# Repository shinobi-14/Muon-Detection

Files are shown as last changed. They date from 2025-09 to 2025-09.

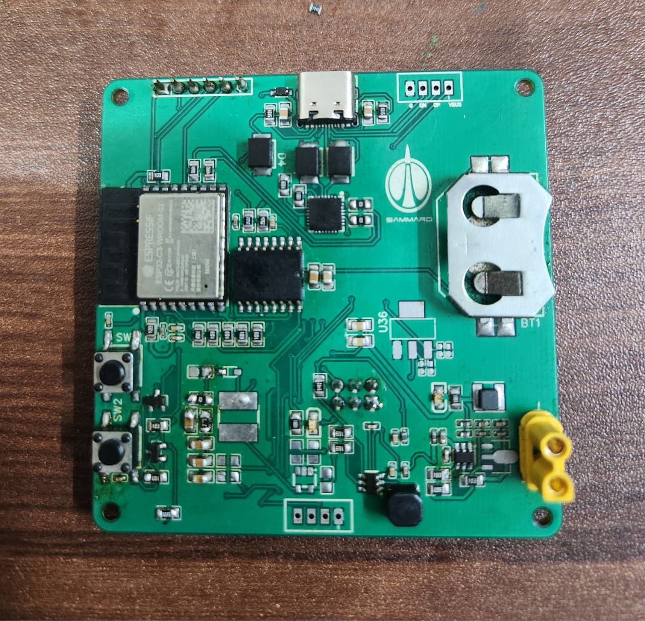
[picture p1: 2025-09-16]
media/images/Soldered_PCB_previews/1.) PCB_top.jpg

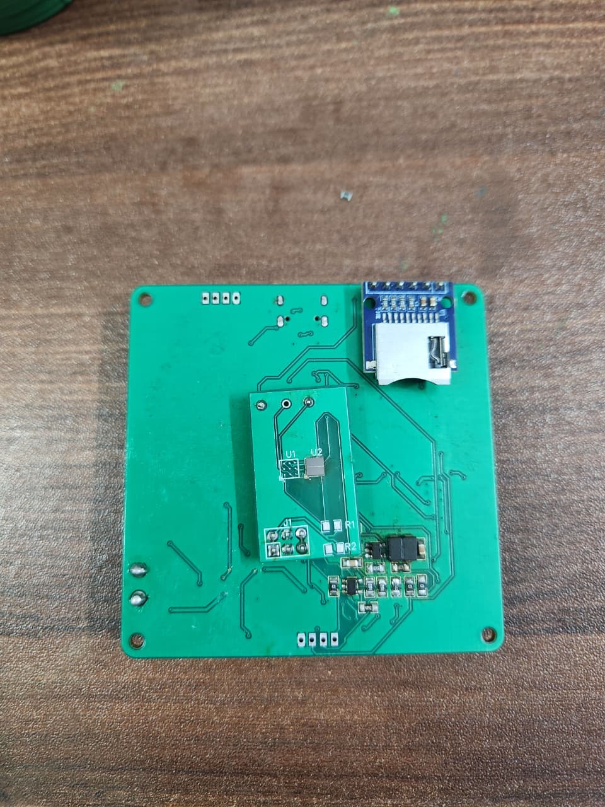
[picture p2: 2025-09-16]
media/images/Soldered_PCB_previews/2.) PCB_bottom.jpg

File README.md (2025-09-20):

# Muon-Detection
Muon-Detection, an independent subsystem of Project STRIVE developed for the SDL Payload Challenge, serves as a payload on the sounding rocket Airavata in IREC 2025.
<div align="center">
  
</div>

The Muon-Detection system incorporates a commercial and a student-designed 3D-printed scintillator (developed in collaboration with IIT Roorkee) to measure muon flux along the rocket's trajectory, enabling performance comparison and supporting real-time tomography simulations for potential non-destructive testing during sonic and supersonic flight.

## Detector Architecture
#### 1. Commercial Scintillator Setup
<div align="left">
  
</div>
    
- Scintillator: BC-408 plastic scintillator (known for its high light yield and fast decay time)
- Photo-detector: 3mm × 3mm BROADCOM's AFBR-S4N33C013  SiPM (Silicon Photomultiplier)
- Associated Electronics

#### 2. Experimental 3D Printed Scintillator
<div align="left">
  
  
</div>

- Scintillation Components: Incorporated 2,5-diphenyloxazole (PPO) and a wavelength shifter.
- Scintillator Fabrication: Used an acrylate photo-curing monomer with aromatic rings as the base matrix.
- 3D Printing Process: Added a small amount of BAPO photo-initiator, poured the mixture into the 3D-printer VAT, and printed 100 µm layers sequentially (on top of each other) to form the final structure.

## SiPM Main PCB
The SiPM PCB is designed to interface with Silicon Photomultipliers (SiPMs) for detecting scintillation events. 
<div align="center">
  
  
</div>

SiPM output signals are typically weak, so this PCB includes a carefully designed amplifier circuit that boosts the signal strength while preserving its integrity. 

The amplifier matches the SiPM’s voltage and current characteristics, ensuring a clean, low-noise signal that maintains the peak amplitude of fast analog pulses for accurate processing by the onboard microcontroller. 

Additionally, the PCB provides stable biasing and reliable signal routing to the data acquisition system, making it a critical component of the payload’s detection and readout chain.

## Repo Structure
The PCB was designed entirely in EasyEDA. I've included the design files, 3D files, gerber, schematic, test codes, media files and testing materials.

To replicate or explore this project, download the repository files and open them in EasyEDA, ensuring all file paths are correctly linked.
    
	1. 3D_files
		a. SIPM main PCB | SIPM small PCB
			- .mtl & .obj 3D exports for 3D visualization and mechanical fit checks.
	
	2. Design_Files 
		a. SIPM main PCB | SIPM small PCB
			i. Altium_Design_files - Exports from EasyEDA for Altium compatibility.
			ii. Autorouter_files - Auto-generated routing results.
			iii. EasyEDA_Design_files - Original PCB designs.
			iv. Export_Netlist_files - Netlists for simulation and validation.
		
	3. Fabrication_files 
		a. SIPM main PCB | SIPM small PCB
			i. Gerber files - Standard files for PCB manufacturing.
			ii. BOMs.csv - List all components used in this project.
			iii. PickAndPlace.csv - Data for automated assembly.
		
	4. Schematics
		a. SIPM main PCB | SIPM small PCB
			i. schematic.pdf - Readable schematic.
			ii. schematic.svg - Scalable/vector schematic.
	
	5.  media
		a. images - Renders, test setups, and PCB visuals.
		b. testing videos - Muon-Detection tests under different conditions.
		
	6. test codes
		All the test codes used during testing.
		
	7. testing materials
		Contains test records, analysis, and performance evaluation of commercial and 3D-printed scintillators.

 ## Components Used
 - AFBR-S4N33C013 SiPM (Silicone Photomultiplier)
 - BC-408 (Plastic Scintillator)
 - 3D-printed Scintillator
 - MIC2288 (DC-DC Boost Converter @ 33V)
 - DS3231 (Real Time Clock)
 - OPA356 (Operational Amplifier)
 - XT30 (Overload connector @ 30A)
 - SD Card Reader module
 - ESP32 C3 (32bit-microcontroller)
 - HT7833 (LDO Regulator @ 3.3V) - Redundant
 - AMS1117 (LDO Regulator @ 5V) - Redundant
 - CP2102 (UART Interface)
 - TPS56321 (Switching regulator @ 3.3V | @ 5V)

## Key Takeaways
1. It is not possible to couple two scintillators together, as there will be an immense amount of light loss at the boundary. 
2. This is the same region where we require large single crystals instead of smaller crystals coupled together. 
3. The scintillator can be coupled to the SiPM using optical-grade silicone gel/glue provided by companies such as Eljen (EJ-550, EJ-552) or Epic crystals.
4. There is a degradation of the additively manufactured scintillator with time. 
5. With temperature fluctuations, the scintillator could potentially lose its scintillation effect and overall effectiveness.
6. The PCB for the payload is designed for signal integrity, but the efficient functioning of the system in the scope of sounding rocket flight might be affected by the level of EM interference in the PCB. Therefore, readings might get affected due to this.
7. The muon detection system relies on the duration during which the rocket descends. There is a potential problem where the system can work efficiently only while it is at a specific altitude for a specific period of time.
8. While testing, I noticed that for BC-408 and 8.2 mm, squiggles are fewer compared to 3.9 mm and 6.2 mm. As the width increases, properly distinct peaks can be observed, which means thicker the sample, the farther the particle can penetrate through, so more efficient production of photons.

## Reference Materials 
- [SiPM Datasheet](https://www.farnell.com/datasheets/3096135.pdf?_gl=1*1ttkvz9*_gcl_au*MTI4NTU5OTYwNS4xNzQzNzAwNDU1)
- [OPA356 Datasheet](https://www.ti.com/lit/ds/symlink/opa356.pdf?ts=1746455532552&ref_url=https%253A%252F%252Fwww.google.com%252F)
- [Peak Detection Circuit](https://www.youtube.com/watch?v=w4531AVjBYY) (Highly Recommended)
- [britishastronomical Youtube](https://www.youtube.com/watch?v=j74CbXHByrY)
- [Front-end Electronics for SiPM](https://physicsopenlab.org/2017/11/28/front-end-electronics-for-sipm/)
- [Cosmic Watch Muon-Detector](https://github.com/spenceraxani/CosmicWatch-Desktop-Muon-Detector-v2/blob/master/PCB_Files/callibration.pdf) (Highly Recommended)
- [RD-Gammaspectra](https://www.youtube.com/watch?v=t7-f01MC4a4&t=58s) (Highly Recommended)
- [Current to Voltage Converotr](https://ecstudiosystems.com/discover/textbooks/basic-electronics/operational-amplifiers/current-to-voltage-converter/)
- [Mini SIPM Driver Board](https://hackaday.io/project/188090-mini-sipm-driver-board)
- [Muon Tomography Simulation](https://github.com/dimitra97/MuonTomographySimulation)
- [ComSAD](https://ar5iv.labs.arxiv.org/html/2110.12500)
- [Data acquisition system for the readout of SiPM arrays](https://ieeexplore.ieee.org/abstract/document/6829735) (Highly Recommended)

Author: Prithvi Raj Singh (shinobi-14)

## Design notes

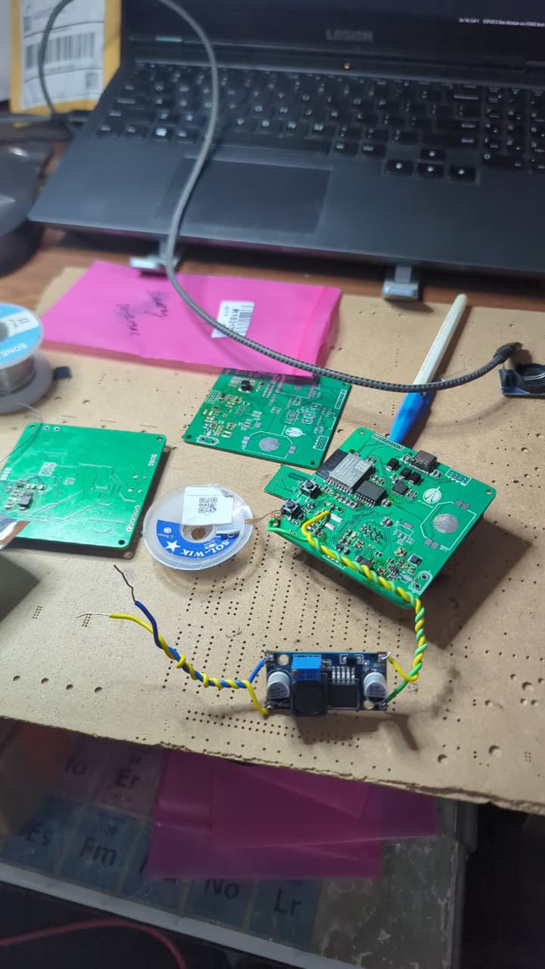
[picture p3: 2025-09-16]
media/images/Workbench.jpg

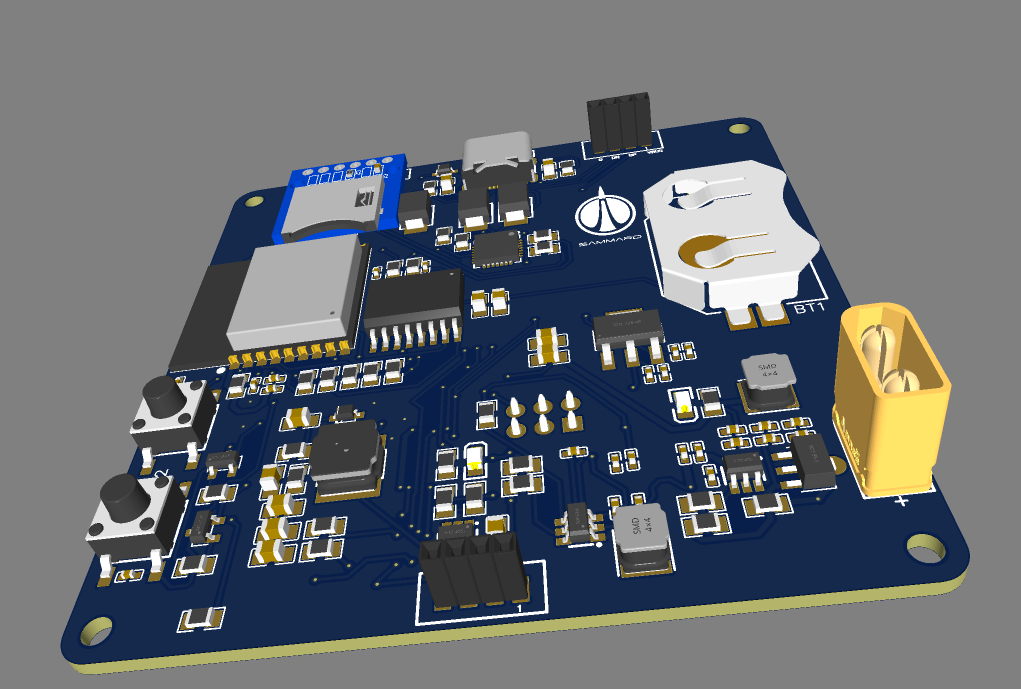
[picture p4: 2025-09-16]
media/images/3D_previews/1.) 3D_SIPM.png

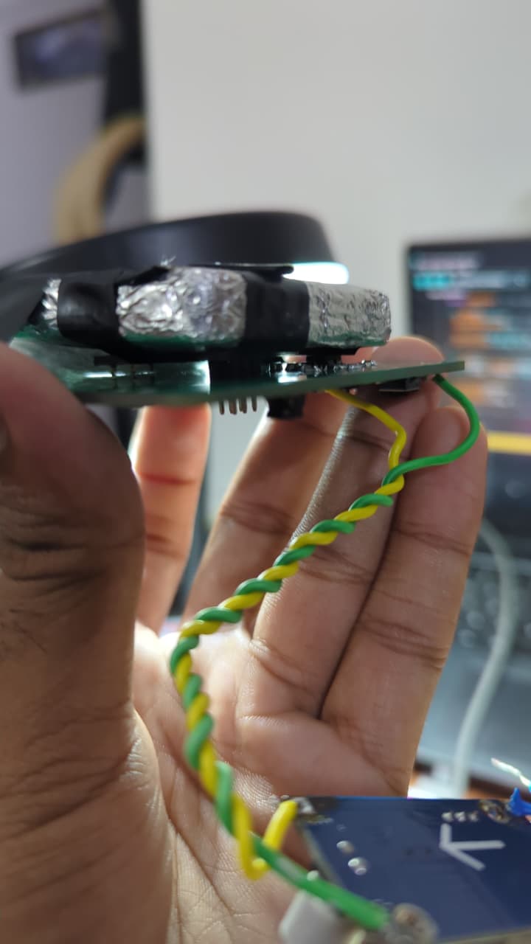
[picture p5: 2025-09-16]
media/images/Scintillator/Scintillator_wrapped_with_foil.jpg

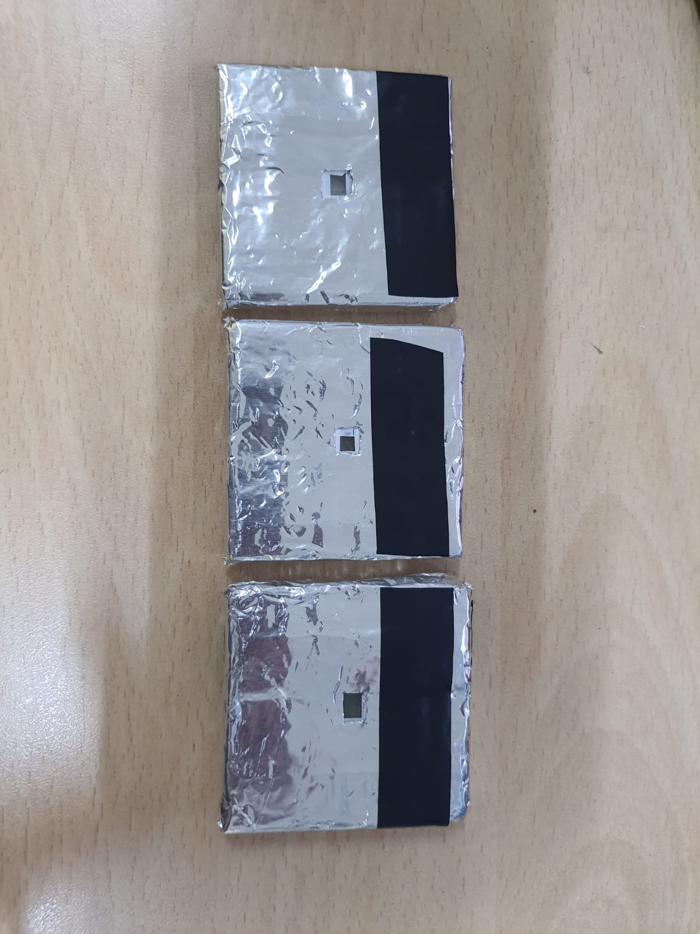
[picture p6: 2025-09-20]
media/images/Scintillator/Scintillator(2).jpg

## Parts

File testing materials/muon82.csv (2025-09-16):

components | package | 1
1.5uH | 603 | 1
AMS 3.3 |  | 1
TPS63030 |  | 1
35.7K | 603
AMS 5
1uF | 805
MCP16311
1.5uH power inductor
56K | 805
10uF | 805
22uH power inductor
220 ohms | 805 | BESSV2
4.7K | 805 | BESSV2
10K | 805 | BESSV2
1N4007 |  | BESSV2
6pF | 603
10uF | 805
100nF | 805
22uF | 805
dual mosfet P
AMS 3.3
5.1K | 805
7.5nH | 402
power usb c
ams 5
1uF | 805
0.1uF | 805
1.2K | 805 | PDB
3.3uH power inductor |  | PDB
20K | 805 | PDB
54.9K | 603 | PDB
12k | 603
0 ohms | 805
130 ohms | 805
100 ohms | 805
10K | 805
0.1uF | 603
0.1uF | 805
10uF | 805
blue led | 805
red led | 805
10uF | 1206
22uF | 1206
1K | 805
esp32 c6
battery charging board
switches
INSPACE BOX - untouched
2.2uF | 603 | SHROTA v2
type c power |  | SHROTA v2
ESD diode | DO214AA | SHROTA v2
100nF | 603 | SHROTA v2
1K | 603
4.7K | 603
22uF | 603
22 ohms | 603
5.1K | 603
HT7833 LDO 3.3 SOT-235
6.5pF | 603
7.5uH | 402
1.5uH | 603
10K | 603
10uF | 603
antenna 915MHz
HT7833 LDO 3.3 SOT-89 3
Diodes 1n4007ws
ws2812b
female to sma

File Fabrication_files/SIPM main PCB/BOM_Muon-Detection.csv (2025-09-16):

ID | Name | Designator | Footprint | Quantity | Manufacturer Part
1 | CR2032 | BT1 | BAT-SMD_CR2032 | 1 | CR2032
2 | 0.1uF | C1,C7,C10,C12,C14 | C0805 | 5 | 0805B203K500NT
3 | 10uF | C2,C8,C11,C13,C16 | C0805 | 5 | 0805B203K500NT
4 | 4.7uF | C3 | C0805 | 1 | 0805B203K500NT
5 | 2.2uF | C4 | C0805 | 1 | 0805B203K500NT
6 | 20nF | C5,C6,C9 | C0805 | 3 | 0805B203K500NT
7 | 1uF | C15,C17 | C0805 | 2 | 0805B203K500NT
8 | XT30UPB-M | CN1 | CONN-TH_XT30UPB-M | 1 | XT30UPB-M
9 | 1N5819WS | D1 | SOD-323_L1.8-W1.3-LS2.5-RD | 1 | 1N5819WS
10 | LBAT54HT1G | D2 | SOD-323_L1.8-W1.3-LS2.5-RD | 1 | LBAT54HT1G
11 | 1N5817W | D3,D7 | SOD-123_L2.8-W1.8-LS3.7-RD | 2 | 1N5817W
12 | SMBJ7.5CA-QH | D4,D5,D6 | DO-214AA_L4.4-W3.6-LS5.3-BI | 3 | SMBJ7.5CA-QH
13 | 2×(4-1) Double female header | H1 | HDR-TH_6P-P2.54-V-F-R2-C3-S2.54-1 | 1 | 2×(4-1) Double female header
14 | 10uH | L1 | IND-SMD_L6.0-W6.0_FNR60XXS | 1 | SWPA6028S100MT
15 | 2.2uH | L2 | IND-SMD_L4.0-W4.0_SMNR4012 | 1 | SWPA4030S3R3MT
16 | 3.3uH | L3 | IND-SMD_L4.0-W4.0_SMNR4012 | 1 | SWPA4030S3R3MT
17 | SD card Reader | P1 | HDR-TH_6P-P2.54-V-F | 1 | 2.54-1*6P母
18 | L8050QLT1G | Q1,Q2 | SOT-23-3_L2.9-W1.3-P1.90-LS2.4-BR | 2 | L8050QLT1G
19 | 10k | R1,R2,R11,R14,R18,R22,R33,R34,R35 | R0805 | 9 | 0805
20 | 10K | R3,R6,R7,R19,R20 | R0805 | 5 | 0805
21 | 2k | R4 | R0805 | 1 | 0805
22 | 33.2k | R5 | R0805 | 1 | 0805
23 | 1k | R8,R31,R32,R43 | R0805 | 4 | 0805
24 | 51k | R9 | R0805 | 1 | 0805
25 | 499 | R10,R13 | R0805 | 2 | 0805
26 | 0805 | R12,R17,R21,R23,R24,R25,R26,R27,R37,R41,R42 | R0805 | 11 | 0805
27 | 5.1k | R15,R16 | R0805 | 2 | 0805
28 | 0Ω | R28,R29 | R0805 | 2 | 0805
29 | 54.9k | R30 | R0805 | 1 | 0805
30 | 22.1K | R36 | R0805 | 1 | 0805
31 | 47.5K | R38 | R0805 | 1 | 0805
32 | 0Ω | R39,R40 | R0805 | 2 | FRC0805P000 TS
33 | SMD Tactile Switch6*6*6mm | SW1,SW2 | SW-SMD_4P-L6.0-W6.0-P4.50-LS9.0_C23873 | 2 | 贴片轻触开关6*6*6mm
34 | JST-PH_4-PIN_HEADER | U1,U17 | JST_B4B-PH_HEADER | 2
35 | 0.1uF | U2,U5,U10,U18,U20,U27,U32,U34,U37,U40 | C0402 | 10 | GRM155R71E103KA01D | SMD Ceramic Capacitor
36 | TPS563201DDCR | U3,U21 | SOT-23-6_L2.9-W1.6-P0.95-LS2.8-BR | 2 | TPS563201DDCR
37 | 10uF | U4,U11,U22,U28,U31,U33,U38,U39 | C0402 | 8 | GRM155R71E103KA01D | SMD Ceramic Capacitor
38 | MIC2288YD5-TR | U6 | TSOT-23-5_L2.9-W1.6-P0.95-LS2.8-BR | 1 | MIC2288YD5-TR
39 | ESP32-C3-WROOM-02-N4(4MB) | U7 | BULETM-SMD_ESPRESSIF_ESP32-C3-WROOM-02-N4-4MB | 1 | ESP32-C3-WROOM-02-N4
40 | 22uF | U8,U9,U24,U25 | C0402 | 4 | GRM155R71E103KA01D | SMD Ceramic Capacitor
41 | 1uF | U12,U13,U35 | C0402 | 3 | GRM155R71E103KA01D | SMD Ceramic Capacitor
42 | OPA356AIDBVR | U14,U15 | SOT-23-5_L3.0-W1.7-P0.95-LS2.8-BR | 2 | OPA356AIDBVR
43 | 0805 SF-RED | U16,U29,U41 | LED0805-RD_RED | 3 | 0805 SF-Red
44 | DS3231 | U19 | SO16W | 1
45 | CP2102 | U23 | QFN-28_L5.0-W5.0-P0.50-TL-EP3.2 | 1 | CP2102
46 | HT7833 | U26 | SOT-89_L4.5-W2.5-P1.50-LS4.2-BR | 1 | HT7833
47 | Sipm2 | U30 | SIPM_REVERSE | 1
48 | AMS117-5V | U36 | AMS117-TOPL | 1
49 | HX TYPE-C 16P 3MD 5A | USB1 | TYPE-C-SMD_HX-TYPE-C-16P-3MD-5A | 1 | HX TYPE-C 16P 3MD 5A

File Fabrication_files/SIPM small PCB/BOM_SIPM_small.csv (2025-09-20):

ID | Name | Designator | Footprint | Quantity
1 | Header-Male-2.54_2x3 | J1 | HDR-TH_6P-P2.54-V-M-R2-C3-S2.54-1 | 1
2 | 0Ω | R1,R2 | R0805 | 2
3 | NO | U1 | SIPM_ORI | 1
4 | Sipm2 | U2 | SIPM_REVERSE | 1

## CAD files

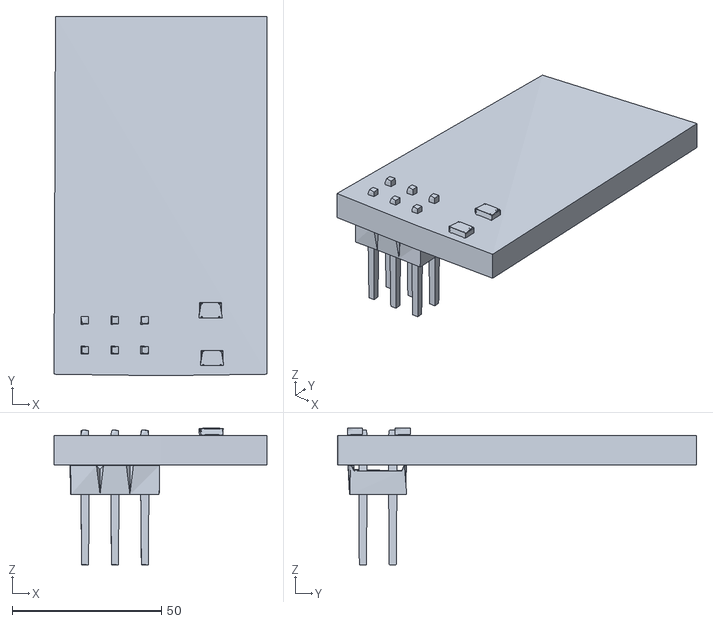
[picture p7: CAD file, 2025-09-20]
3D_Files/SIPM small PCB/OBJ_SIPM_small.obj
71.3 x 120.3 x 45.8

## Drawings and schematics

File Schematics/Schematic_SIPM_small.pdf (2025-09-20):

# SIPM PCB

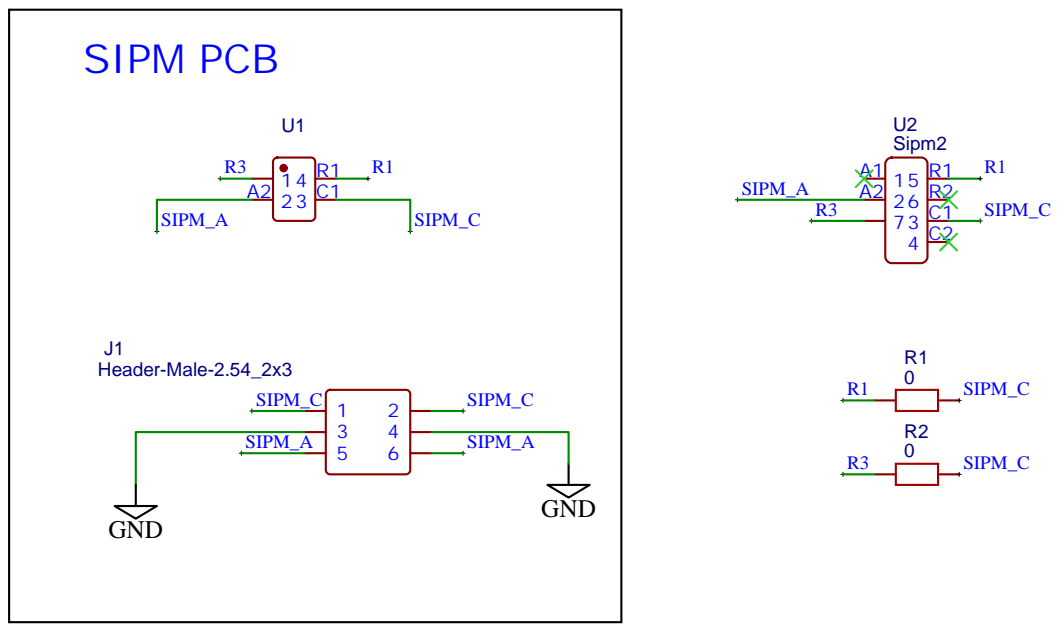
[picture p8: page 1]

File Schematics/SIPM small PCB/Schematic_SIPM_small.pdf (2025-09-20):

# SIPM PCB


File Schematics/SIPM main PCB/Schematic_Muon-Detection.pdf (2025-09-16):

# DC-DC Booster

# GND GND ³V3

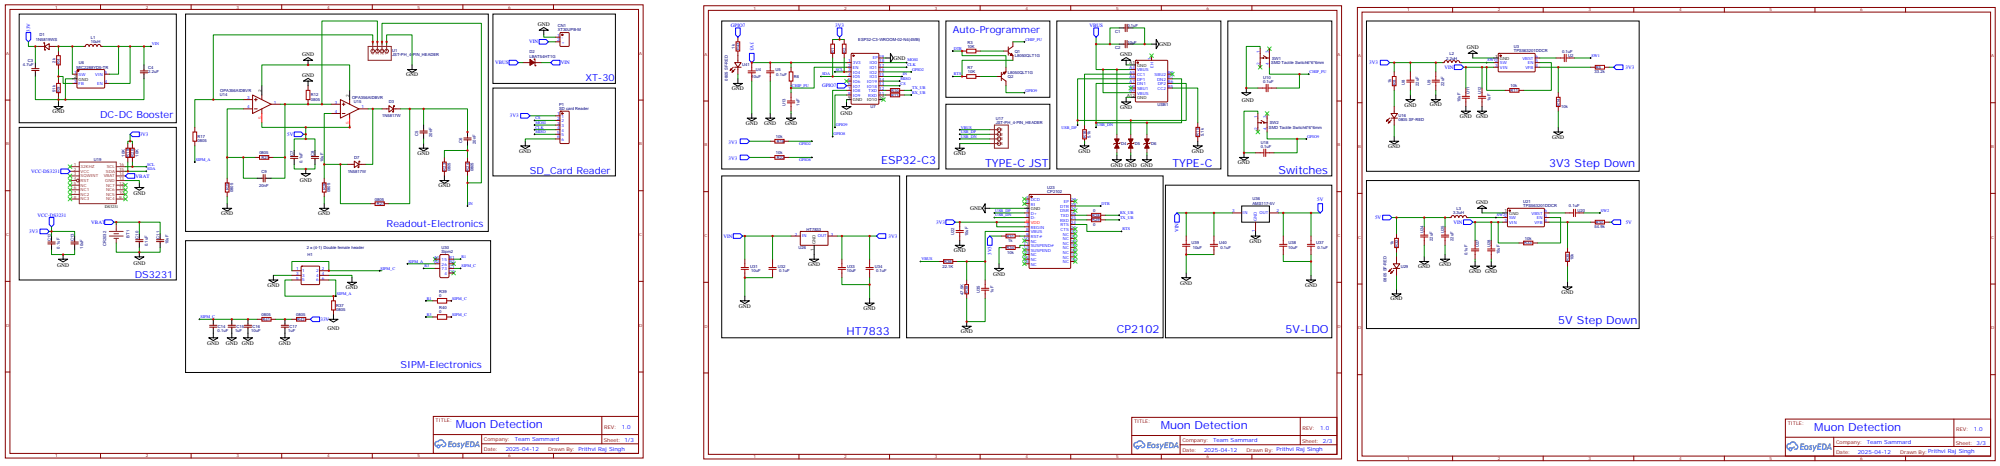
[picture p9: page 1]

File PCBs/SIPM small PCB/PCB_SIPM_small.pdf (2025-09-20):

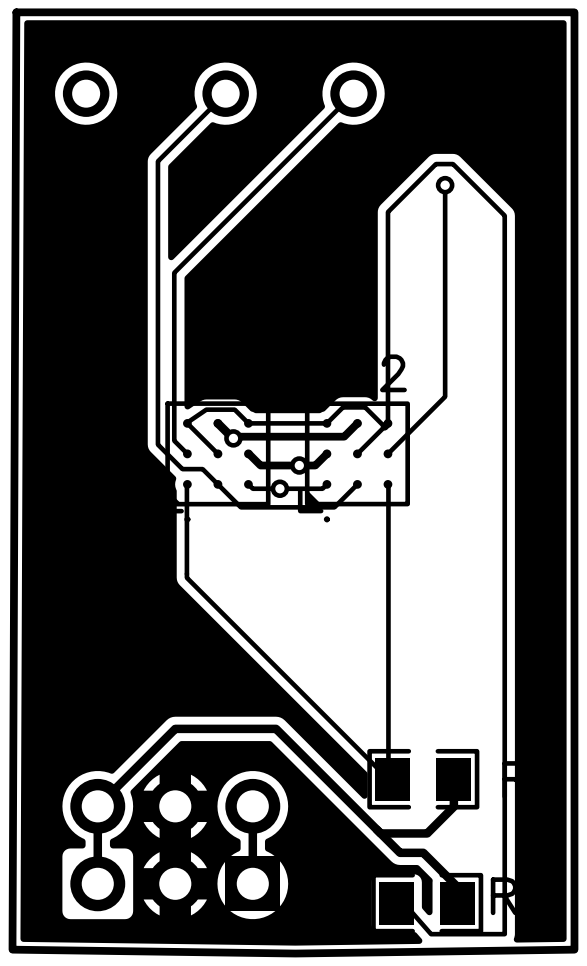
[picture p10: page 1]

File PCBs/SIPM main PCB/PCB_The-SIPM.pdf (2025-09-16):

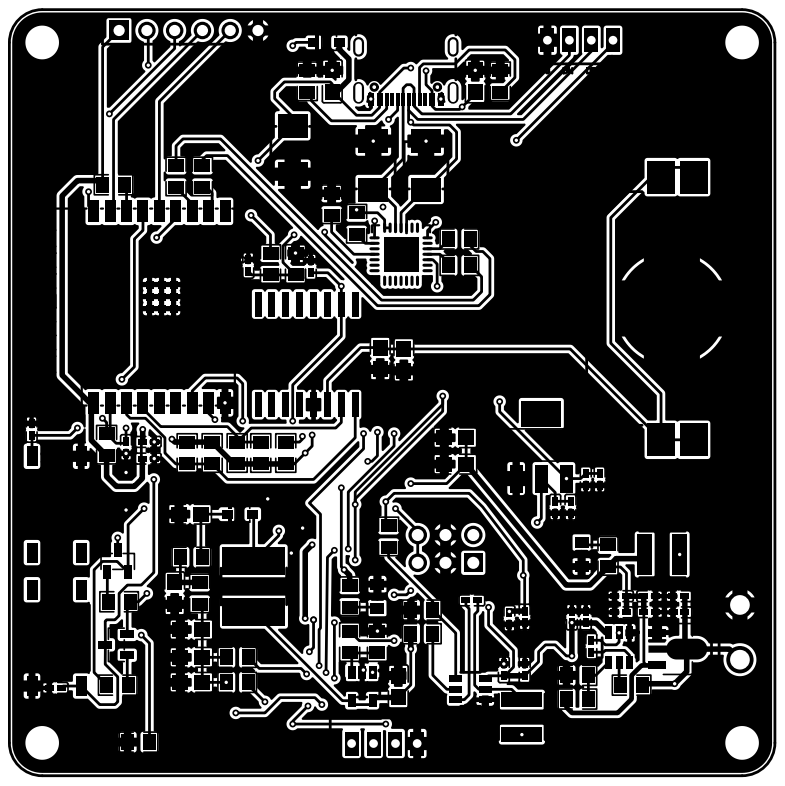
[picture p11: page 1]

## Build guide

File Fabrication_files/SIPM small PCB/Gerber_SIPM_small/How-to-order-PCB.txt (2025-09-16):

How to Order PCB

Please refer to:
https://docs.easyeda.com/en/PCB/Order-PCB

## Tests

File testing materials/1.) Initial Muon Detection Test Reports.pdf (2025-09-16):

TEST1: SiPM pre-amplification tested

AIM: To mainly check if the SiPM is giving output and amplification is happening or not.

EXPT:
- Prototype built with OVA356 as a non-inverting amplifier.
- Phone Flash light is used to see if the current increases proportionally. It was increasing as expected. The fall time is also very quick (in nanoseconds).

OBSERVATION AND INFERENCE:
- As the flashlight photons hit on SiPM the signal gets increased and the preamplification occurs.
- As the lab was noisy (from external light) there was noise in the signal.
- Even still we could observe a gain of around 3 times.
- Noise after amplification came around 25mV.
- Flashlight hits after amplification came around 72mV.

PHOTOS ATTACHED:

1.)Setup →

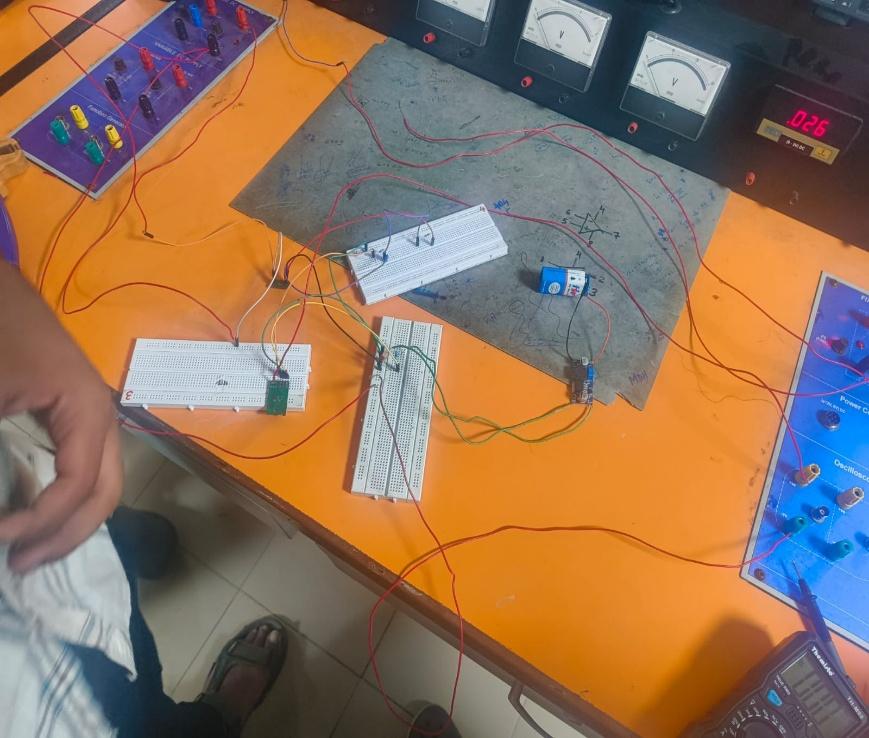
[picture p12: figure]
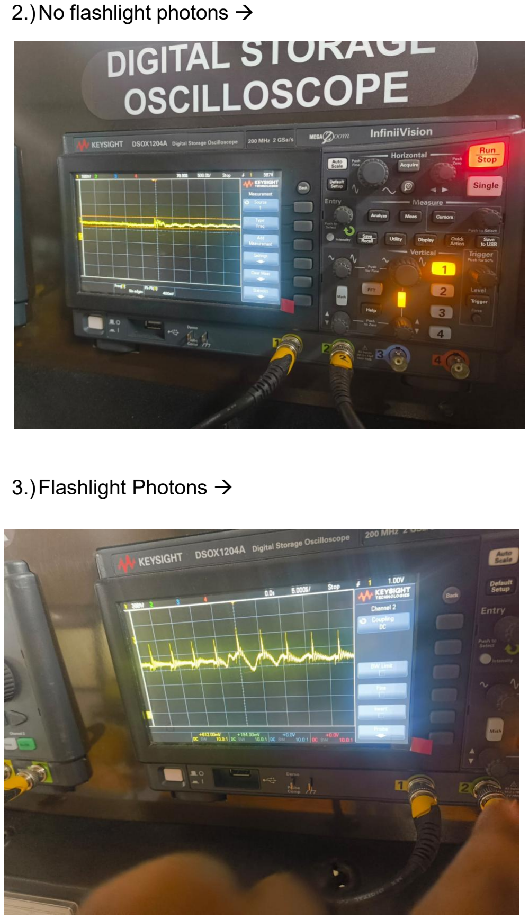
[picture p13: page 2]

2.)No flashlight photons →

3.)Flashlight Photons →

RESULTS AND OPINION:

As it was the first circuit prototype, it was an average result. Still a lot of work is left in optimizing the circuit results

TEST2: Pre-amplification tested with function generator

AIM: To mainly check if the amplification is happening properly or not.

EXPT:
- Prototype built with OVA356 as an inverting amplifier.
- Square wave is given as an input.

OBSERVATION AND INFERENCE:
- It was not amplifying properly, maybe because of some loose connections.
- But after debugging we saw amplification.

PHOTOS ATTACHED:

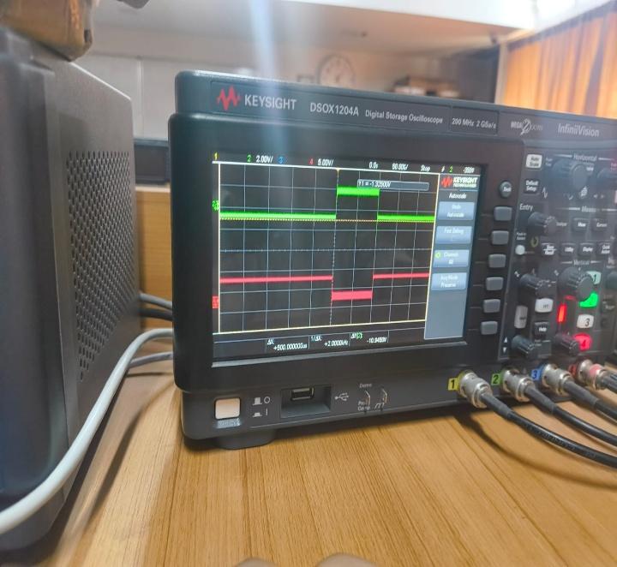
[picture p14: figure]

RESULTS AND OPINIONS:

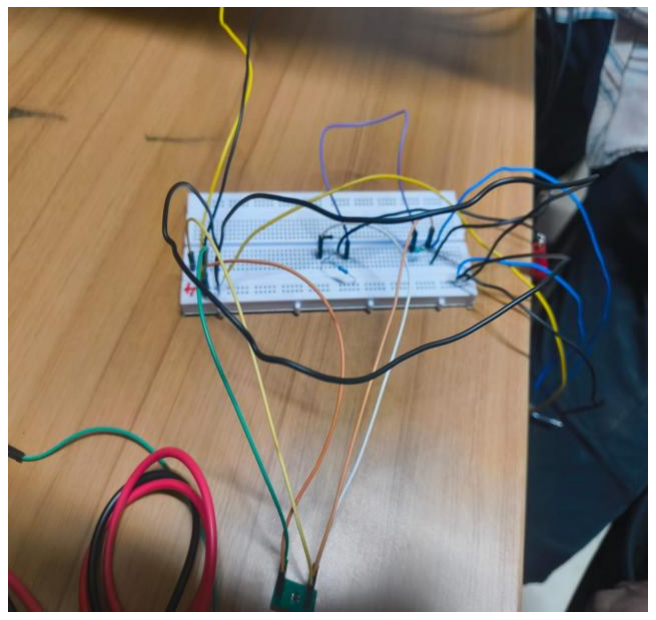
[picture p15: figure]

As the amplification circuit is working, now time to test the second part of the circuit, that is peak and hold circuit.

TEST3: Preamp + Peak-hold circuit with function generator

AIM: To check if the preamp + peak-hold circuit is working properly or not.

EXPT:
- Prototype built with 2 OVA356s and 2 PN junction diodes (Schottky not available).
- Square wave is given as an input.
- Given a voltage of 1Vp-p to 2Vp-p as PN diode works only if voltage is more than 0.7V.

OBSERVATION AND INFERENCE:
- The results were not that good as hold time is very low.
- Maybe because the capacitors are discharging very fast.
- Also had a problem that output was not coming properly.
- Sometimes error outputs came.
- Maybe wrong resistors, capacitors value used.
- Tried integrated testing, output was full of errors.

PHOTOS ATTACHED:

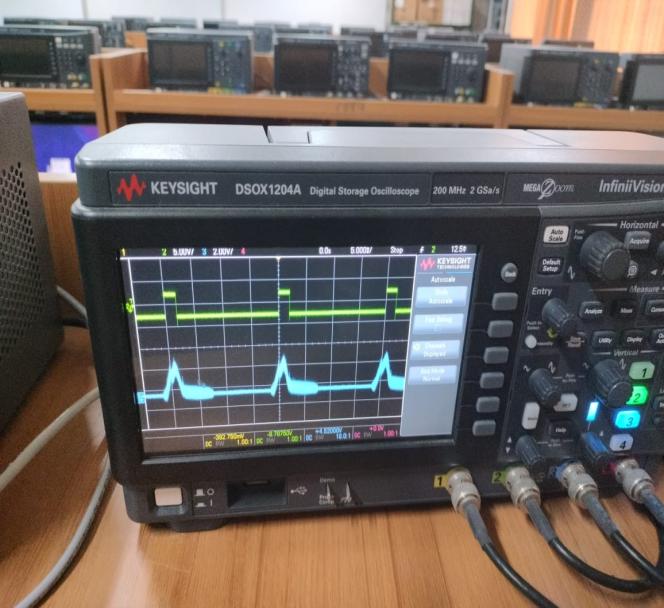
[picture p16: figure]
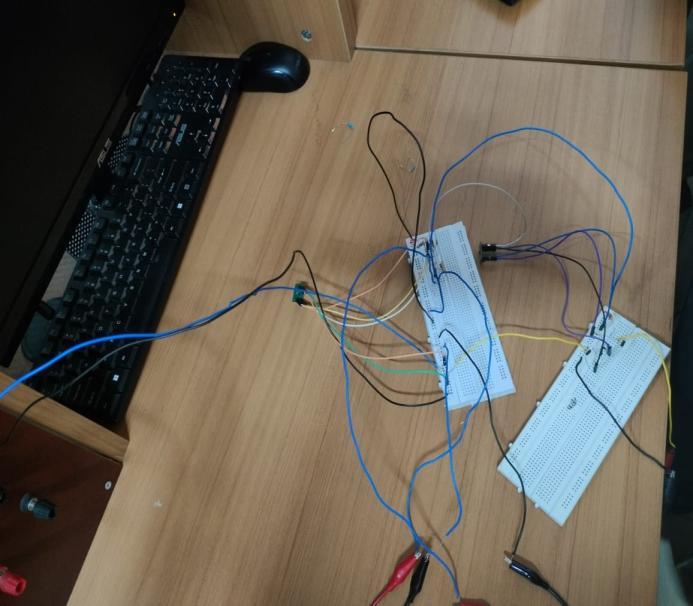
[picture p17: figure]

The Error Output:

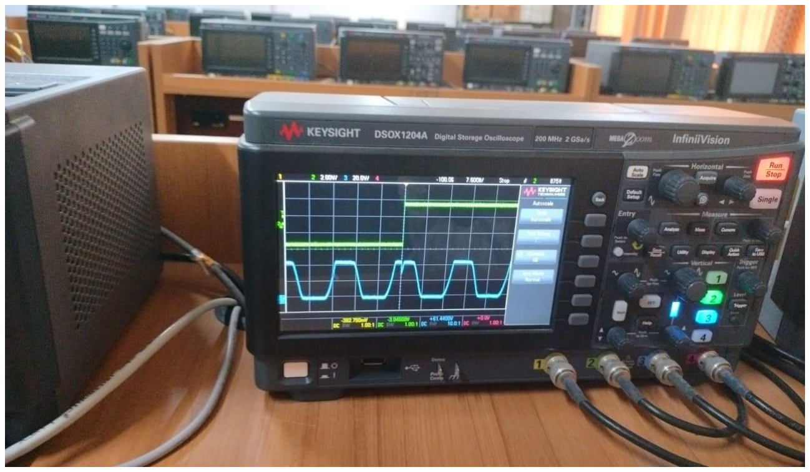
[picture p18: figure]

RESULTS AND OPINIONS:
Only once the output came kind of good, the others could not even be understood. Some outputs didn't even make sense, might be wrong connection or maybe the circuit is wrong. Have to check it all.

TEST4: Preamp + Peak-hold circuit with function generator

AIM: To check if the preamp + peak-hold circuit is working properly or not.

EXPT:
- Prototype built with 2 OVA356s and 2 PN junction diodes (Schottky not available).
- Square wave and pulse wave are given as an input.
- Given a voltage of 2Vp-p as PN diode works only if voltage is more than 0.7V.

OBSERVATION AND INFERENCE:
- The results were very good this time as the output was hold for some time .
- Changing the capacitors worked.
- The output was coming as expected.
- No error output was observed.
- Integrated testing was done.
- The results were satisfactory every time the testing was done.
- Duty cycles were varied.

PHOTOS ATTACHED:

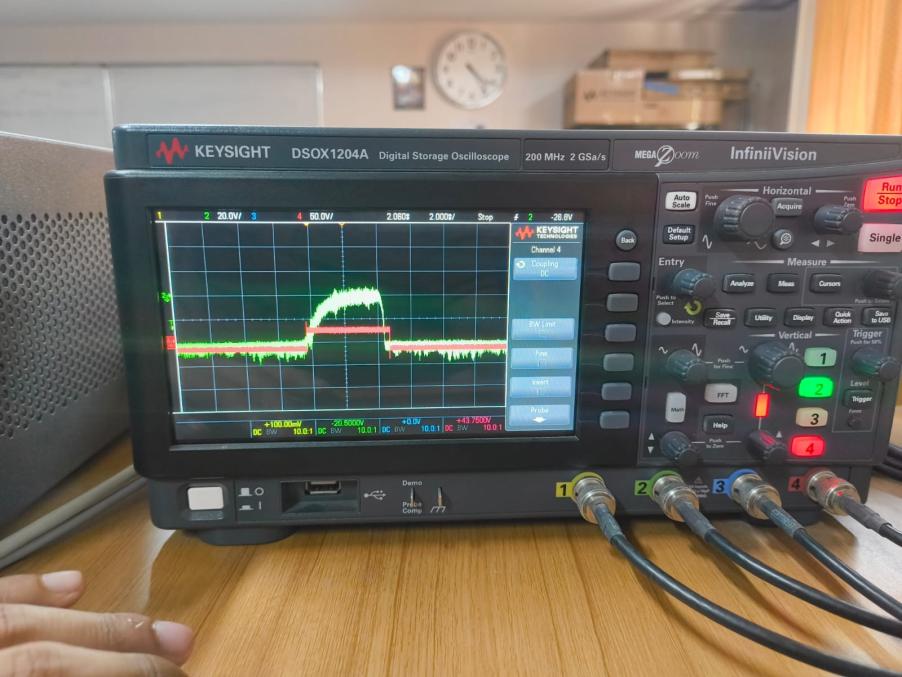
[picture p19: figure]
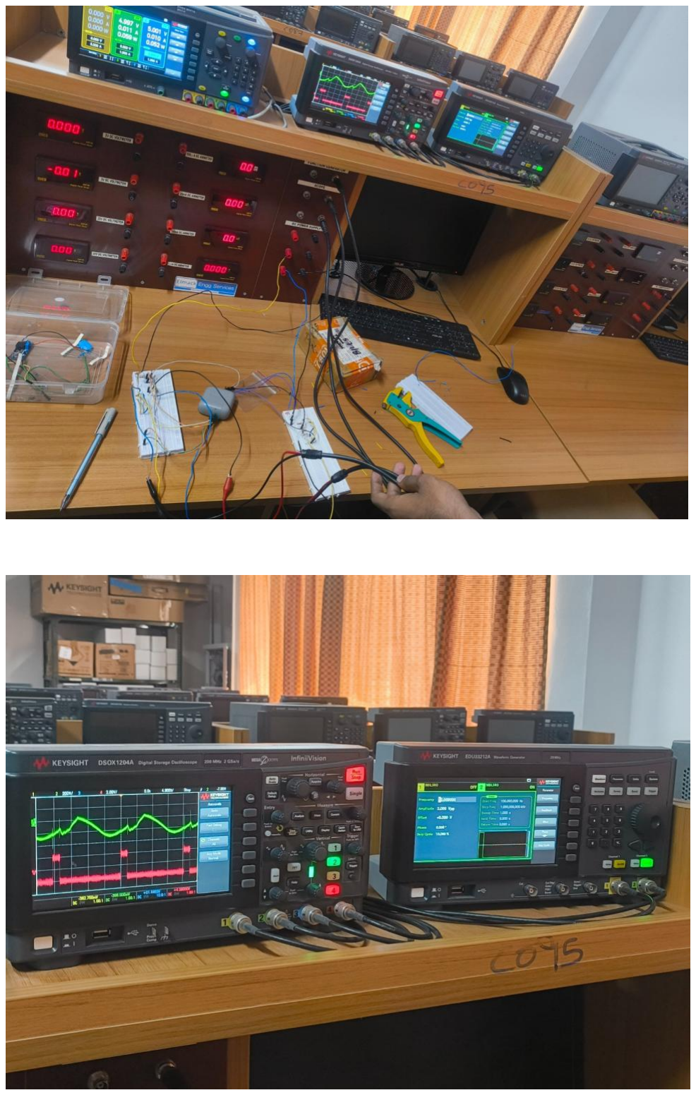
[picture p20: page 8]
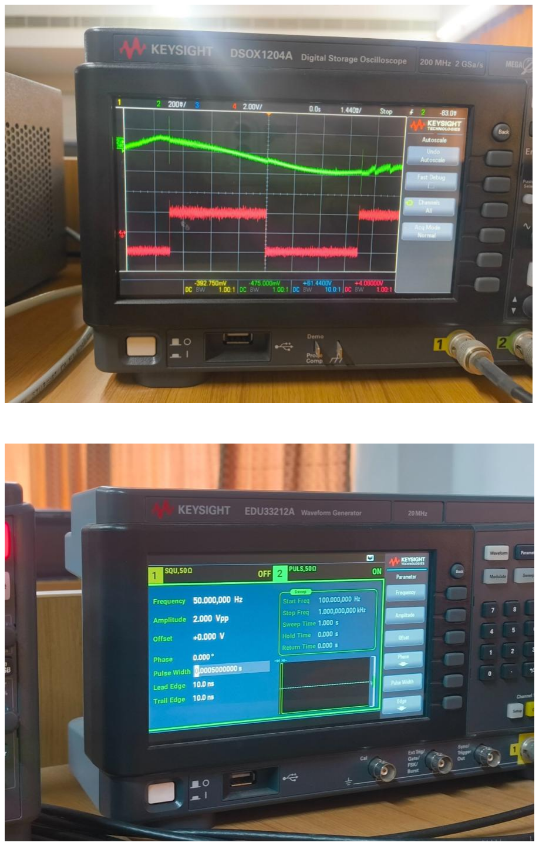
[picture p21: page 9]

The schematic that was followed:


RESULTS AND OPINIONS:
The output was correct every time the tests were done. Now to optimize the circuit that is to add a SiPM and a scintillator in the next test.

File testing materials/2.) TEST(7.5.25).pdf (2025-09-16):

# TEST@7/5/2025


Using perfboard:

1) USING FUNCTION GENERATOR {input 50mV,freq 10Hz}

INPUT: pulse with 10ns rise time; 50ns delay time

Green – output | Red – input


OBSERVATIONS:

- There is a time delay of 3ms between the pulse signal and the output signal because of the diodes used.
- Germanium diodes {precision diodes OA79} are used.
- Schottky diodes have the least possible delay, while germanium diode has delay in them.


The output alone:

The output reached around 2V and the peak was held for 41ms.


The output voltage and hold time increased slightly when the input was 100mV.


A zoomed in version with 500ns scale revealed the characteristics of peak and hold circuit.


A zoomed-out image at 5ms scale reveals the amplification and the delay time associated with it.

2) Using SiPM with flash light setup {phone’s flashlight was used}


OBSERVATIONS:

- Delay time between input and output increased to 60ms maybe because of less voltage produced by SiPM and the external environment factors like lab’s lighting (assumption) or maybe because of the not very sharp increase in the input signal because of the torchlight.


Another case where the delay time is around 70ms.

There were lot of cases (where we forgot to take the photos of other cases), and the delay was in the range of 50ms - 80ms.


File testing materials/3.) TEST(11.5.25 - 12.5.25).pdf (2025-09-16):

# TEST@11 MAY 2025 - 12 MAY 2025


With BC408 Plastic Scintillator

SETUP:

- BC408 wrapped in aluminum and then SiPM is placed and the setup is covered in black tape.
- The test was conducted in a dark room and vaseline was not used as we did not have it.
- The number of muon counts was noted for 1 min & it was repeated for 5 times .


1)

A total of 3 hits were noted.

2)

A total of 4 hits were noted.

3)


A total of 3 hits were noted.

(I forgot to take the photos of the other 2 tests but similar results of 3 hits and 4 hits happened)

OBSERVATION:
- The count is matching with the average count that should hit a 5cm x 5cm area scintillator according to cosmic watch.

FOR 3D PRINTED SCINTILLATOR:

We used the 3.9 mm scintillator and it was used for 3 times with a duration of 1

min each.

1)


Two times muon hit.

2)


1 muon hit.

3) Muon hits count - 2

Note:
- The delta voltage is quite less because of the usage of 3.9mm,
- The code should be optimized so as to prevent drifts that occur over time.
- Because of the usage of Germanium diodes instead of schottky, the delta voltage is less.

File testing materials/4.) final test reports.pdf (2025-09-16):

1) Prototype testing - Breadboards :


→ The SiPM PCB


The connections are made on the breadboard, and the circuit's reliability is tested using a function generator and an oscilloscope.

The Readout electronics comprises the following subsystems:


- Signal Amplification: The output signal from the SiPM is typically weak, so an amplifier circuit is needed to boost the signal strength. This is crucial for ensuring that the signal is strong enough for further processing by the microcontroller.
- Amplifier Design: The amplifier circuit is designed to match the characteristics of the SiPM, ensuring it can handle the specific voltage and current requirements of the photodetector while also providing a clean, noise-free signal to the onboard microcontroller.
- Peak detector circuit Design: The circuit is designed so as to capture and maintain the peak amplitude of the analog input. We have implemented an active peak detector using OPA356 op-amp.


The green signal is the input fed from the function generator, and the cyan signal is the output that can be seen in the oscilloscope. As the output suggest,s the peak is being detected and getting held for some time.

2) Prototype testing - Perfboard:


The circuit is built on a perf board, and the connections are tested using a function generator and an oscilloscope. The perfboard reduces the noise experienced in breadboards


The red signal is the input, and the green signal is the output. A delay between the input signal and the output signal can be observed because of the use of PN diodes instead of Schottky diodes.

3) Prototype testing - Perfboard + microcontroller :

The perfboard circuit is used with the SiPM PCB and the scintillators to detect muons using an ESP32 microcontroller. The circuit remains the same, and the output of the readout circuitry is given as input to the analog pin of the ESP32. The scintillator is completely wrapped in aluminum foil and then black taped.

The scintillators used are BC408 and additive-manufactured scintillators. The scintillators were fabricated using an acrylate photo-curing monomer as the base matrix. The monomer has aromatic rings in its structure. For scintillation, 2,5-diphenyloxazole (PPO) was used along with a wavelength shifter. To induce photo-curing, a photo-initiator (BAPO) was used in a small amount. The cocktail was poured into the VAT of the 3D-printer, and 100 μm layers were printed on top of each other to form the desired structure.


The spike in the voltage can be translated as the muon count that hits the scintillator area.


4) Graphing the results for all the scintillator samples

The same setup is used to quantify the number of muon hits for 5 minutes.

Sample 1: BC408

Sample 2: Additive-manufactured scintillator with a width of 3.9mm


Sample 3: Additive-manufactured scintillator with a width of 6.2mm

Sample 4: Additive-manufactured scintillator with a width of 8.2mm

5) Moving into final assembly - PCB production and testing


The PCB has been designed and then assembled.


When a muon interacts with the scintillator material, a brief burst of light is produced, which is then detected by the photodetector (such as a SiPM). This is represented by the sharp spike in the voltage signal. A quick electrical pulse is produced by this interaction, and the oscilloscope shows this as a clear peak. The system can determine how many muons have passed through the scintillator area over time because each of these voltage spikes represents a single muon event. Researchers can measure muon flux and investigate associated cosmic ray phenomena by examining the frequency and features of these spikes.

### TIMELINE

Ideation; Prototype; Design; Testing& Prototyping; Final Design; 2024 to January; designed around

MUON DETECTION SUBSYSTEM

The PCB and the
entire subsystem
have been
assembled during
May 2025

The ideation took
place around

Research took place
from November

The circuit was
designed in
February 2025 and

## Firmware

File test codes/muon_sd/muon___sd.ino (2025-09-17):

#include <SPI.h>
#include <SD.h>

// Sensor pin (use stable ADC1 pin)
#define SENSOR_PIN 3  


#define SD_CS_PIN 18    // CS pin for SD card
#define SD_MOSI 0
#define SD_MISO 19
#define SD_SCK  1

SPIClass customSPI(2);  // or HSPI if needed

File dataFile;

void setup() {
  Serial.begin(115200);
  analogReadResolution(12);  // 12-bit ADC (0-4095)

  // Initialize custom SPI bus
  customSPI.begin(SD_SCK, SD_MISO, SD_MOSI, SD_CS_PIN);

  if (!SD.begin(SD_CS_PIN, customSPI)) {
    Serial.println("SD card initialization failed!");
    while (1);  // Halt
  }
  Serial.println("SD card initialized.");

  // Create file and write CSV header if it doesn't exist
  dataFile = SD.open("/datalog.csv", FILE_WRITE);
  if (dataFile) {
    if (dataFile.size() == 0) {
      dataFile.println("Raw ADC Value,Voltage (in V)");
    }
    dataFile.close();
  } else {
    Serial.println("Error opening datalog.csv for writing.");
  }
}

void loop() {
  int rawValue = analogRead(SENSOR_PIN);
  float voltage = (rawValue / 4095.0) * 3.3;

  // Print to Serial
  Serial.printf("%d,%.3f\n", rawValue, voltage);

  // Append data to SD card
  dataFile = SD.open("/datalog.csv", FILE_APPEND);
  if (dataFile) {
    dataFile.printf("%d,%.3f\n", rawValue, voltage);
    dataFile.close();
  } else {
    Serial.println("Error writing to datalog.csv");
  }

  delay(500);  // Sample every 500 ms
}

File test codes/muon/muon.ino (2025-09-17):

#define SENSOR_PIN 3  // ADC-capable pin (e.g., GPIO34, 35, 32, etc.)

void setup() {
  Serial.begin(115200);      // Start serial communication
  analogReadResolution(12);  // Set ADC resolution: 12 bits = 0-4095

  Serial.print("Raw ADC Value,");
  Serial.println(",Voltage (in V)");
}

void loop() {
  int rawValue = analogRead(SENSOR_PIN);  // Read raw ADC value
  float voltage = (rawValue / 4095.0) * 3.3;  // Convert to voltage (assuming 3.3V reference)

  
  Serial.print(rawValue);
  Serial.print(",");
  Serial.println(voltage, 3);  // Print voltage with 3 decimal places

  delay(500);  // Delay for readability
}

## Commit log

2025-09-20 adding the small PCB
2025-09-20 adding the main PCB design files
    [Autorouter_The-SIPM-(1).dsn, Autorouter_The-SIPM-(2).dsn, Schematic_Muon.schdoc, The-SIPM-(1).pcbdoc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]
2025-09-20 adding SIPM main design files
    [Autorouter_The-SIPM-(1).dsn, Autorouter_The-SIPM-(2).dsn, Schematic_Muon.schdoc, The-SIPM-(1).pcbdoc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]
2025-09-20 removing old files
    [BOM_Muon-Detection.csv, BOM_SIPM_small.csv, Drill_NPTH_Through.DRL, Drill_PTH_Through.DRL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]
2025-09-20 adding new files
    [Autorouter_SIPM_small.dsn, SIPM_small.pcbdoc, Sheet1.schdoc]
